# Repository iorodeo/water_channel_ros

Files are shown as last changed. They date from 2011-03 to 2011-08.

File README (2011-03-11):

# Install Ubuntu:
# http://www.ubuntu.com/desktop/get-ubuntu/download
# ubuntu-10.10-desktop-amd64

# Install Ubuntu packages
sudo apt-get install build-essential python-yaml cmake subversion wget python-setuptools mercurial

# ROS Installation
sudo sh -c 'echo "deb http://packages.ros.org/ros/ubuntu maverick main" > /etc/apt/sources.list.d/ros-latest.list'
wget http://packages.ros.org/ros.key -O - | sudo apt-key add -
sudo apt-get update
sudo apt-get install ros-diamondback-desktop-full

# Install the standalone program rosinstall
sudo easy_install -U rosinstall
sudo chmod -R a+rwx /usr/local/lib/python2.6/dist-packages/rosinstall*

# Clone water_channel_ros respository into ~/mercurial/
# Instructions at https://bitbucket.org/iorodeo/water_channel_ros/

# Install water_channel_ros from local repository
cd ~
mkdir ros
rosinstall ~/ros/ /opt/ros/diamondback
rosinstall ~/ros/ ~/mercurial/water_channel_ros/
echo "source ~/ros/setup.bash" >> ~/.bashrc

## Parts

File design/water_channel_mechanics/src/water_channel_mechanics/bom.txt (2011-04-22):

-*- mode:org -*-
#====================================================================#
#============================= bom.txt ==============================#
#                                                                    #
# Autogenerated using ros_cad. Hand editing this file is not         #
# advisable as all modifications will be lost when the program which #
# generated this file is re-run.                                     #
#====================================================================#

| ! | item number | name | description | dimensions | vendor | part number | quantity | cost |
|-
| | 1 | airbearing_mount_plate | Mounts air bearing carriage to t_slotted beam | x: 7.000, y: 7.500, z: 0.500 | ? | ? | 1 | 0.00 |
| | 2 | loadcell_mount_plate | Mounts loadcell to t_slotted beams | x: 6.000, y: 1.000, z: 0.125 | ? | ? | 2 | 0.00 |
| | 3 | pillowblock_mount_plate | Mounts pillowblocks to sleds | x: 7.750, y: 5.000, z: 0.250 | ? | ? | 10 | 0.00 |
| | 4 | slider_mount_plate | Mounts t_slotted beams to air bearing slider | x: 1.000, y: 6.000, z: 0.125 | ? | ? | 2 | 0.00 |
| | 5 | pillowblock | Rail bearings and mounts | x: 4.750, y: 3.500, z: 3.750 | LeeLinear | SPB-24-OPN | 10 | 0.00 |
| | 6 | 1010-double | T-Slotted L Bracket | bracket_type: double | McMaster | 47065T169 | 12 | 5.58 |
| | 7 | 1010-single | T-Slotted L Bracket | bracket_type: single | McMaster | 47065T223 | 32 | 3.98 |
| | 8 | 2020-double | T-Slotted L Bracket | bracket_type: double | McMaster | 47065T176 | 16 | 5.96 |
| | 9 | cushion | Protects the air bearing carriage | x: 1.500, y: 6.500, z: 0.250 | McMaster | 9013K153 | 2 | 15.94 |
| | 10 | submersible_mount | Holds the submersible tube | x: 3.000, y: 2.125, z: 2.000 | McMaster | 47065T207 | 1 | 51.91 |
| | 11 | laser_sensor_long_range | Micro-Epsilon optoNCDT ILR long range distance sensor | x: 5.670, y: 3.898, z: 2.008 | Micro-Epsilon | ILR1182-30(01) | 1 | 0.00 |
| | 12 | laser_sensor_short_range | Micro-Epsilon short range distance sensor | 100mm | Micro-Epsilon | optoNCDT1302 | 1 | 0.00 |
| | 13 | RAB6 | Non-motorized air bearing slide | slide travel: 4 | Nelson Air Corp. | RAB6 | 1 | 4095.00 |
| | 14 | laser_sensor_long_range_mount_plate_bottom | Mounts long range laser sensor to t_slotted beams | x: 4.000, y: 7.000, z: 0.236 | Pololu | ? | 1 | 0.00 |
| | 15 | laser_sensor_long_range_mount_plate_top | Mounts long range laser sensor to t_slotted beams | x: 4.000, y: 7.000, z: 0.236 | Pololu | ? | 1 | 0.00 |
| | 16 | laser_sensor_long_range_target_plate | Target for the long range distance sensor | x: 10.000, y: 10.000, z: 0.236 | Pololu | ? | 1 | 0.00 |
| | 17 | laser_sensor_short_range_mount_plate | Mounts short range laser sensor to t_slotted beams | x: 3.250, y: 4.250, z: 0.236 | Pololu | ? | 1 | 0.00 |
| | 18 | laser_sensor_short_range_target_plate | Target for the short range distance sensor | x: 6.000, y: 4.250, z: 0.236 | Pololu | ? | 1 | 0.00 |
| | 19 | 1010-003.000 | T-Slotted Extrusion | l: 3.000 | Prime Resource | ? | 4 | 0.00 |
| | 20 | 1010-005.000 | T-Slotted Extrusion | l: 5.000 | Prime Resource | ? | 2 | 0.00 |
| | 21 | 1010-006.000 | T-Slotted Extrusion | l: 6.000 | Prime Resource | ? | 5 | 0.00 |
| | 22 | 1010-010.624 | T-Slotted Extrusion | l: 10.624 | Prime Resource | ? | 4 | 0.00 |
| | 23 | 1020-006.000 | T-Slotted Extrusion | l: 6.000 | Prime Resource | ? | 1 | 0.00 |
| | 24 | 1020-008.000 | T-Slotted Extrusion | l: 8.000 | Prime Resource | ? | 3 | 0.00 |
| | 25 | 2040-032.000 | T-Slotted Extrusion | l: 32.000 | Prime Resource | ? | 1 | 0.00 |
| | 26 | 2040-050.000 | T-Slotted Extrusion | l: 50.000 | Prime Resource | ? | 3 | 0.00 |
| | 27 | test_submersible | Submersible used for testing | 12V | Sevylor | U120BLK-00-000 | 1 | 39.99 |
| | 28 | loadcell | Low Single PT Load Cell | 2Kg | TransducerTechniques | LSP-2 | 1 | 110.00 |
|-
| # | | | | | | | total |:=(@I$quantity..@II$quantity)*(@I$cost..@II$cost);%.2f;N

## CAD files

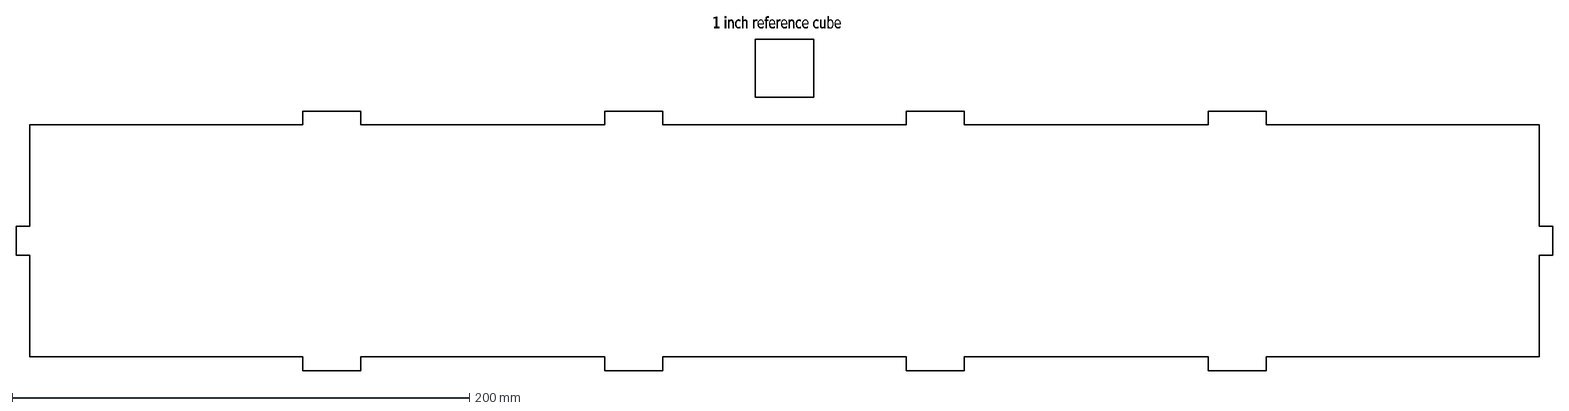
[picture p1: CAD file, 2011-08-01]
design/enclosures/dxf/controller_enclosure/v1p0/controller_enclosure_front.dxf
1\~inch\~reference\~cube

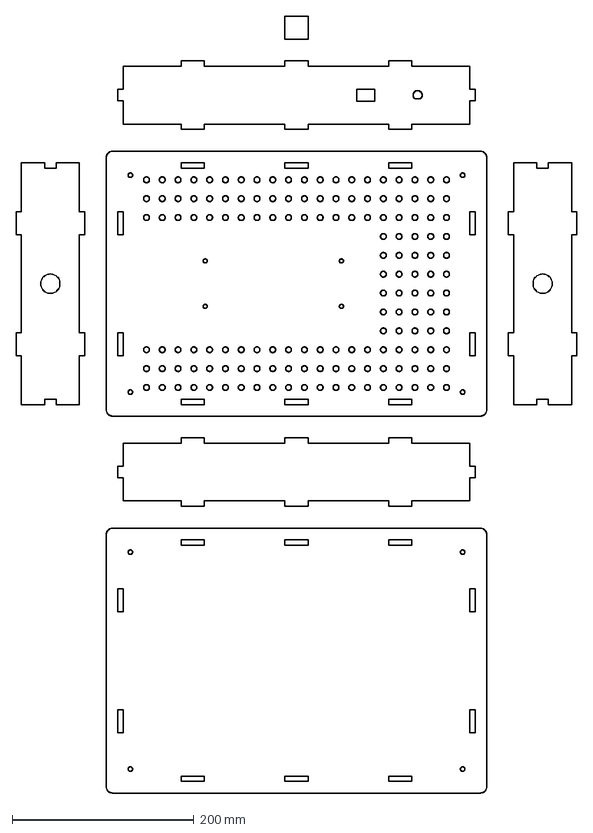
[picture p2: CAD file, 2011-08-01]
design/enclosures/dxf/test_motor_enclosure/v1p0/test_motor_enclosure.dxf
617.4 x 855.2 mm

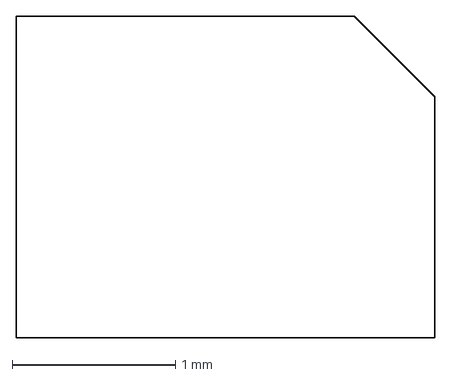
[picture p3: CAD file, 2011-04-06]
design/water_channel_mechanics/src/water_channel_mechanics/laser_sensor_short_range/laser_sensor_short_range.dxf
2.56 x 1.97 mm

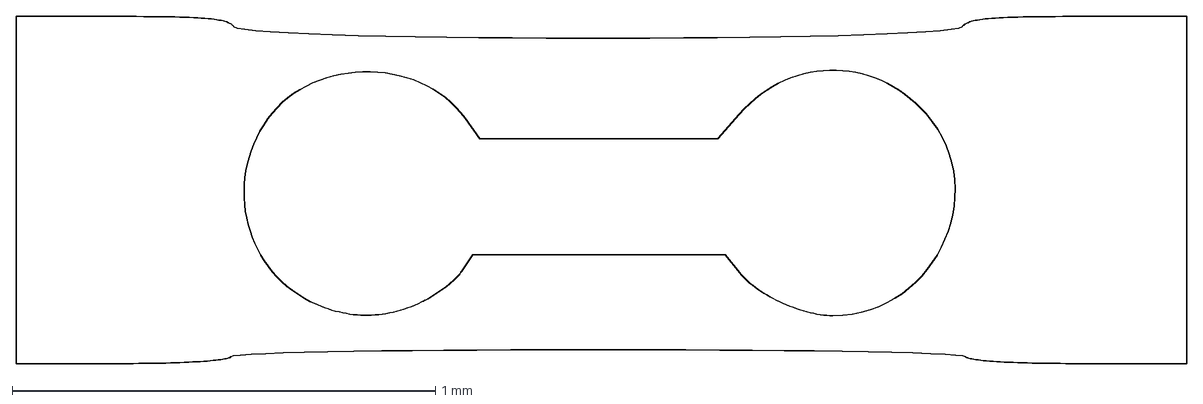
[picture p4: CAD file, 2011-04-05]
design/water_channel_mechanics/src/water_channel_mechanics/loadcell/loadcell.dxf
2.77 x 0.82 mm

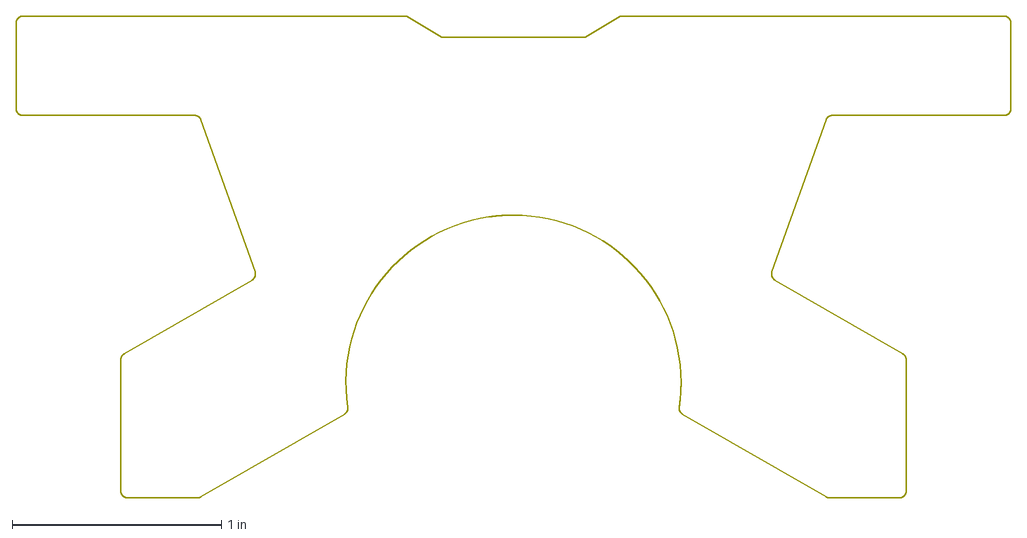
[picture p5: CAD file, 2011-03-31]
design/water_channel_mechanics/src/water_channel_mechanics/pillowblock/pillowblock.dxf
4.75 x 2.30 in

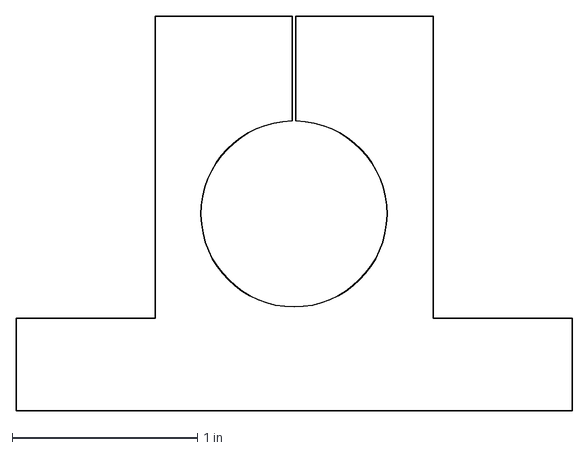
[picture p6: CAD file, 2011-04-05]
design/water_channel_mechanics/src/water_channel_mechanics/submersible_mount/submersible_mount.dxf
3.00 x 2.13 in

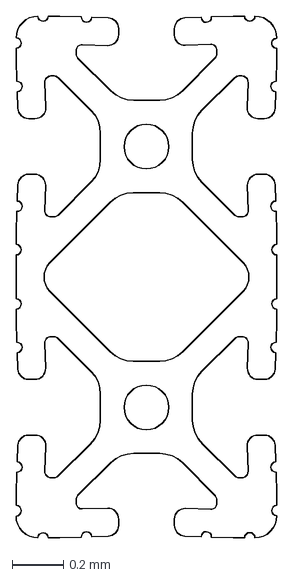
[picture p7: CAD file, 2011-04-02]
design/water_channel_mechanics/src/water_channel_mechanics/t_slotted/extrusion/1020.dxf
1.02 x 2.03 mm

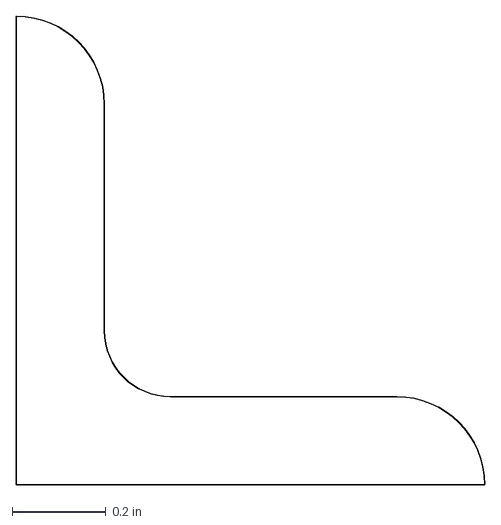
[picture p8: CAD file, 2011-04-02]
design/water_channel_mechanics/src/water_channel_mechanics/t_slotted/lbracket/1010.dxf
1.00 x 1 in

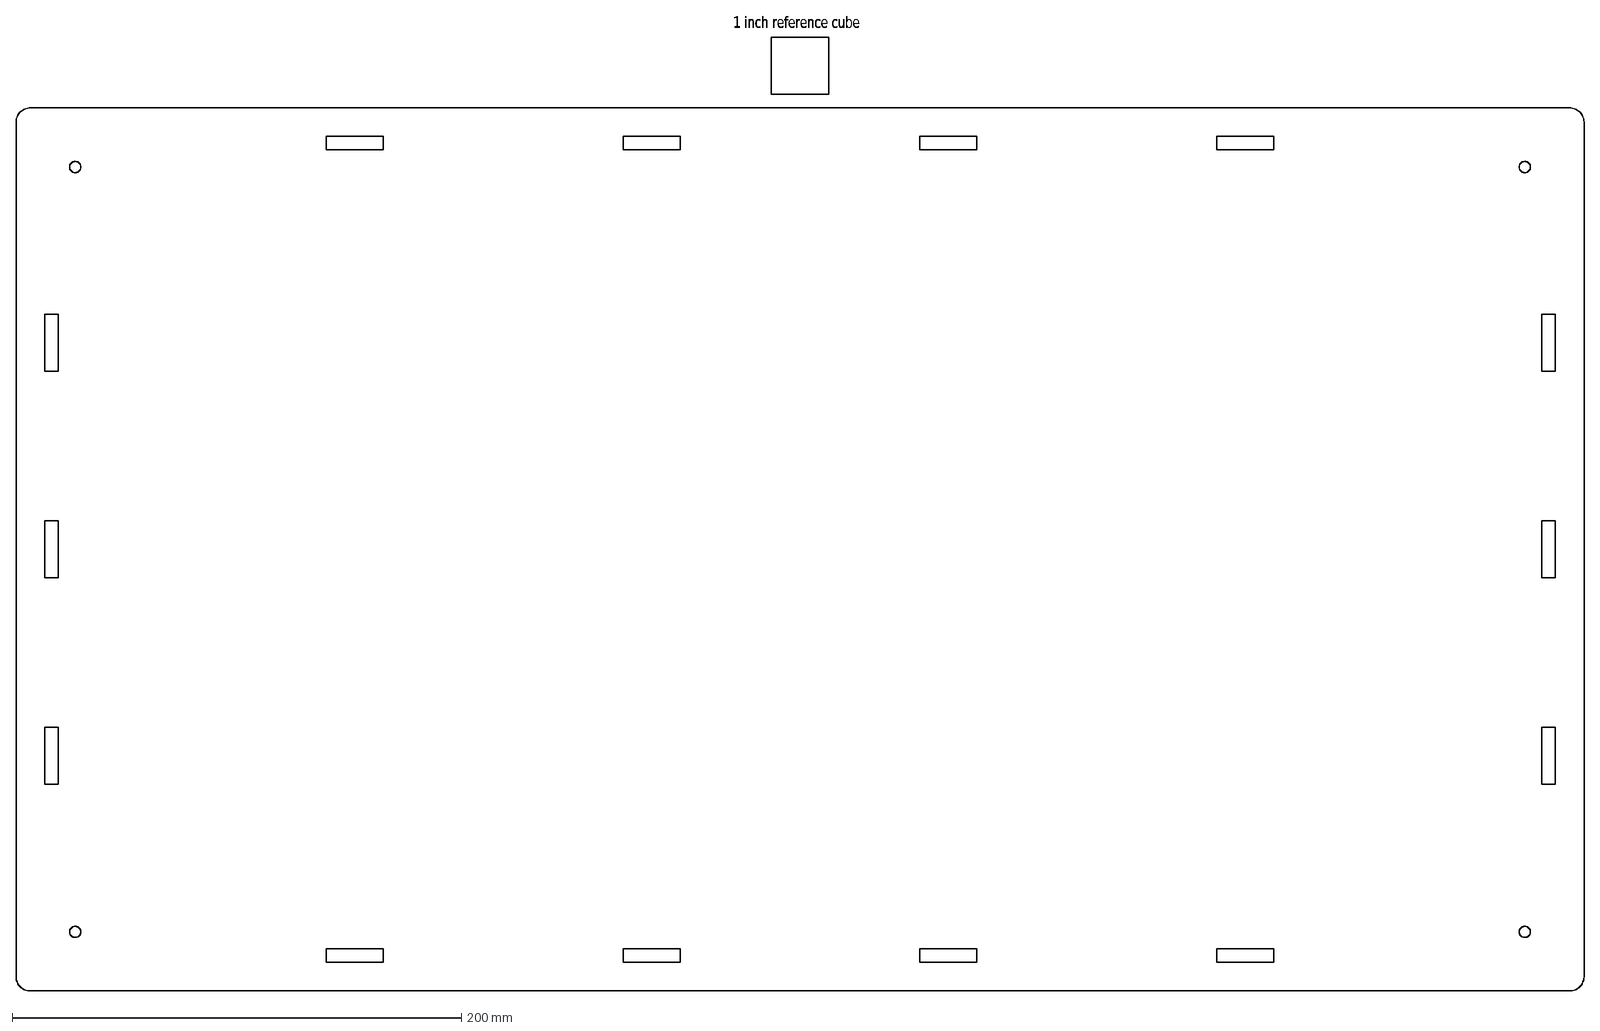
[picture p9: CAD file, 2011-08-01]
design/enclosures/dxf/controller_enclosure/v1p0/controller_enclosure_top.dxf
1\~inch\~reference\~cube

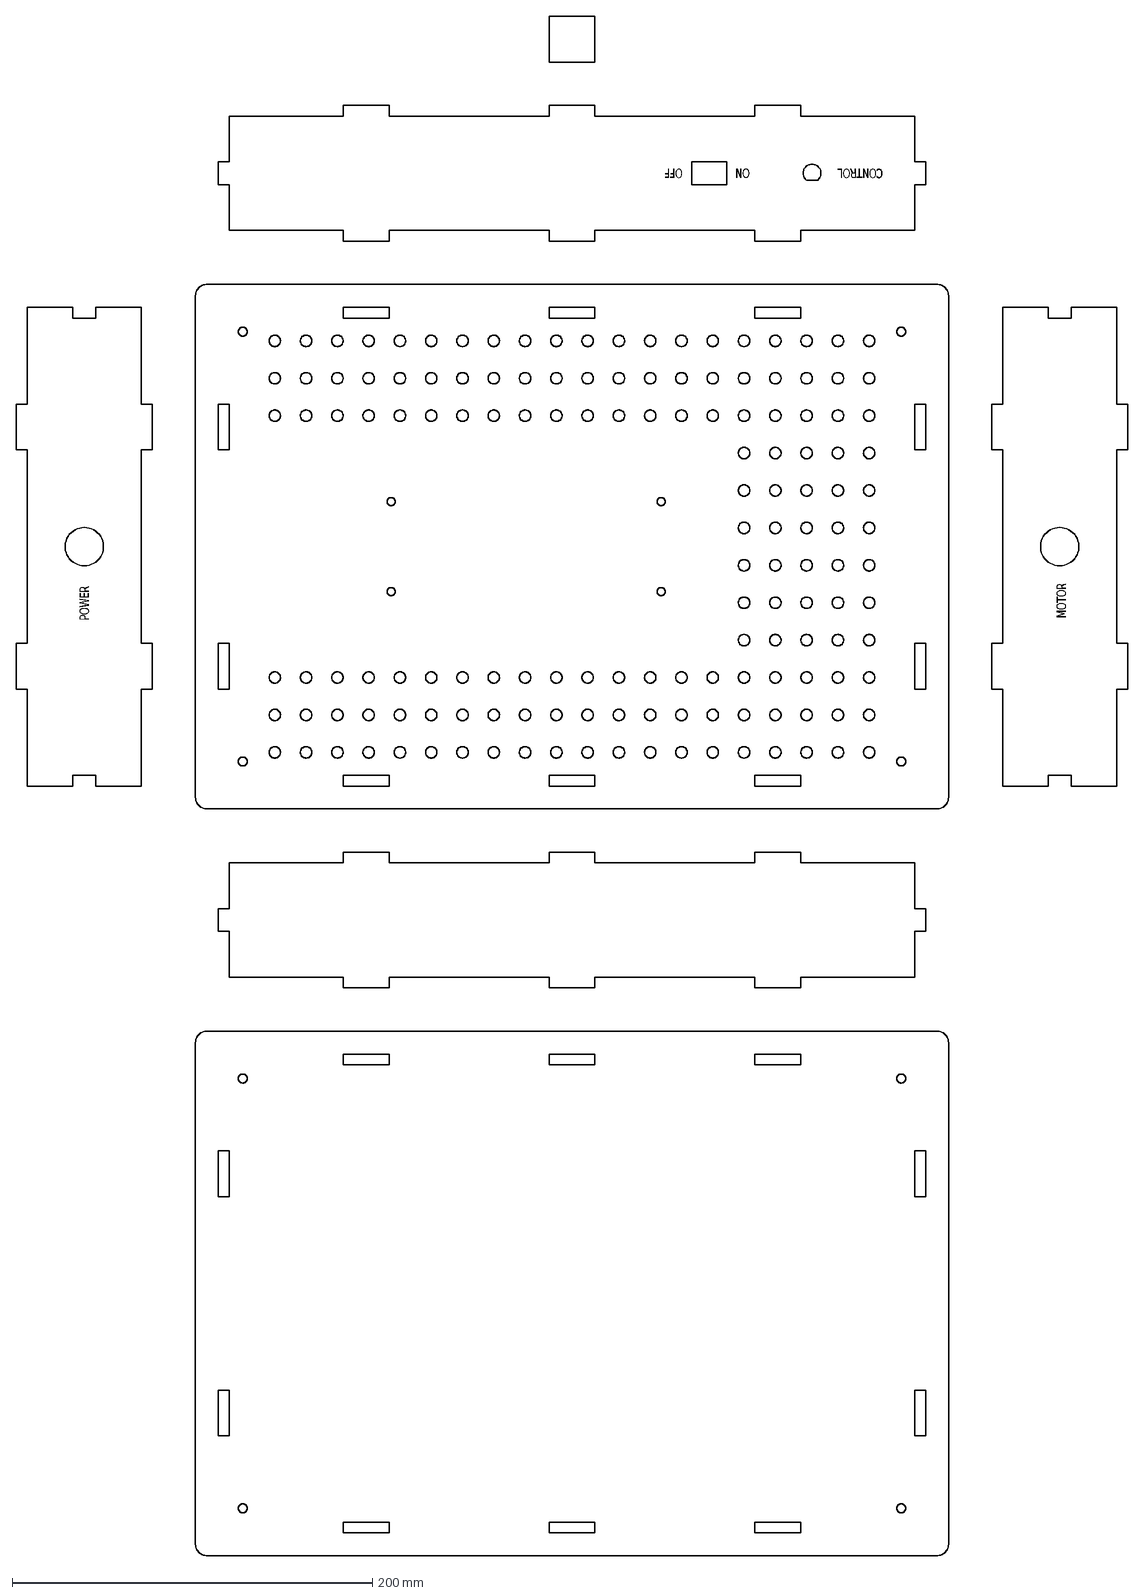
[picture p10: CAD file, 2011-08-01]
design/enclosures/dxf/test_motor_enclosure/v1p0/test_motor_enclosure_w_engrave.dxf
POWER
CONTROL
ON
OFF
MOTOR

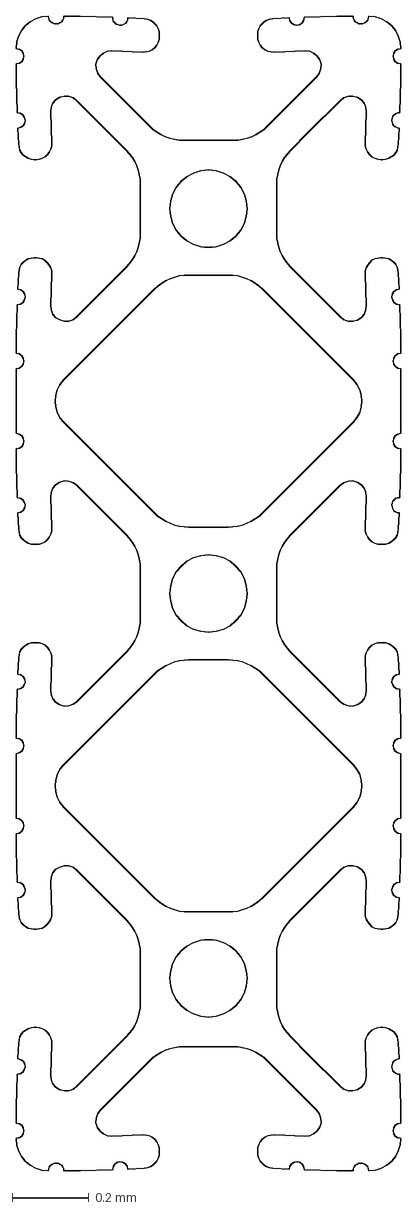
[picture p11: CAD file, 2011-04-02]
design/water_channel_mechanics/src/water_channel_mechanics/t_slotted/extrusion/1030.dxf
1.00 x 3.00 mm

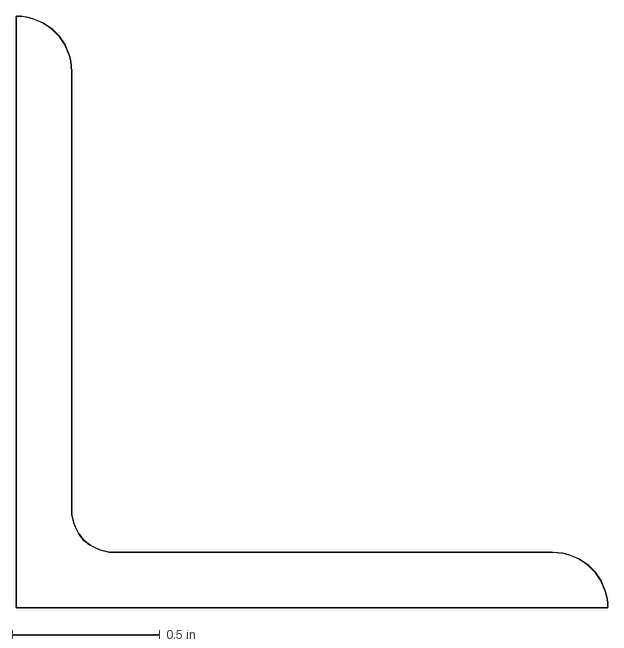
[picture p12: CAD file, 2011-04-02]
design/water_channel_mechanics/src/water_channel_mechanics/t_slotted/lbracket/2020.dxf
2.00 x 2.00 in

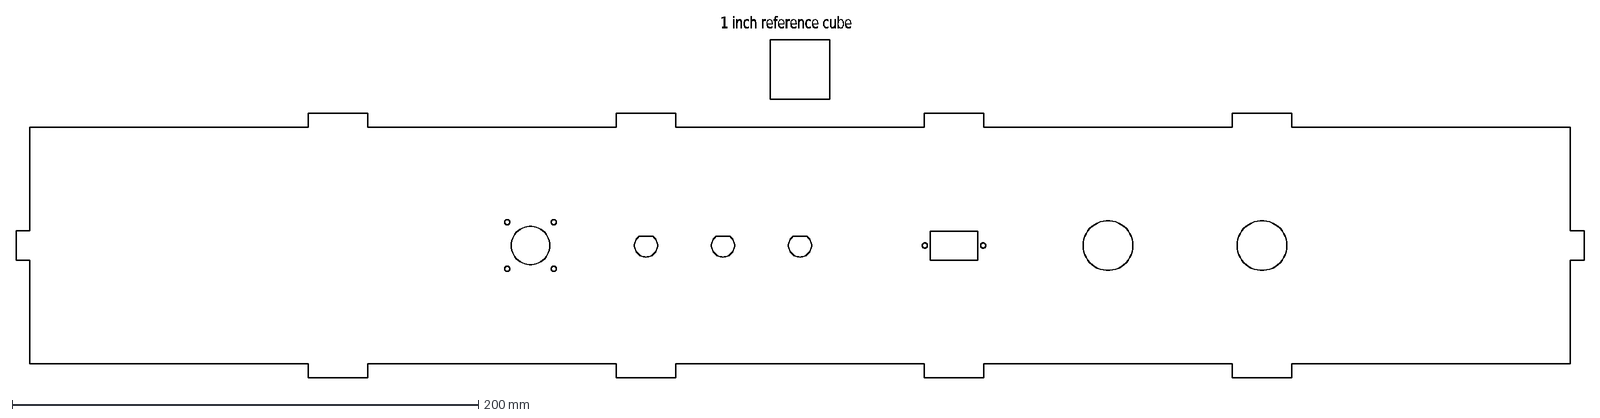
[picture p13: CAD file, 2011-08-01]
design/enclosures/dxf/controller_enclosure/v1p0/controller_enclosure_back.dxf
1\~inch\~reference\~cube

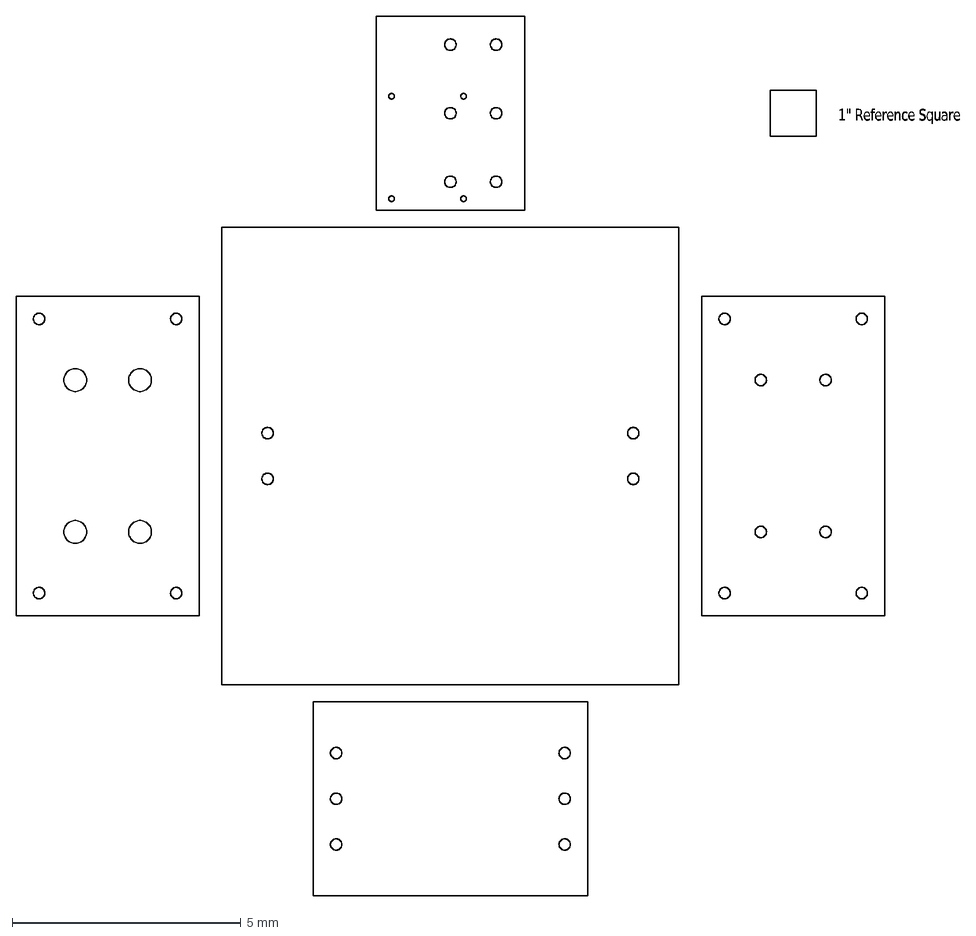
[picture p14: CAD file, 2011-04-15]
design/water_channel_mechanics/src/water_channel_mechanics/export_files/laser_cut_parts.dxf
1"\~Reference\~Square

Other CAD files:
design/enclosures/dxf/kill_switch_enclosure/kill_switch_enclosure.dxf
design/water_channel_mechanics/src/water_channel_mechanics/export_files/cushion.dxf
design/water_channel_mechanics/src/water_channel_mechanics/export_files/cushion_mm.dxf
design/water_channel_mechanics/src/water_channel_mechanics/t_slotted/extrusion/3060.dxf
design/enclosures/dxf/controller_enclosure/v1p0/controller_enclosure_bottom.dxf
design/enclosures/dxf/controller_enclosure/v1p0/controller_enclosure_left.dxf
design/enclosures/dxf/controller_enclosure/v1p0/controller_enclosure_right.dxf
design/water_channel_mechanics/src/water_channel_mechanics/export_files/airbearing_mount_plate.dxf
design/water_channel_mechanics/src/water_channel_mechanics/export_files/airbearing_mount_plate.stl
design/water_channel_mechanics/src/water_channel_mechanics/export_files/loadcell_mount_plate.dxf
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

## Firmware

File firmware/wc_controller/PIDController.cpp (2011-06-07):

#include "PIDController.h"

PIDController::PIDController() {
    pGain = 0.0;
    dGain = 0.0;
    iGain = 0.0;
    ffGain = 0.0;
    lastError = 0.0;
    integralTerm = 0.0;
    isFirstUpdate = true;
    outputMax = PID_DFLT_OUTPUT_MAX;
    outputMin = PID_DFLT_OUTPUT_MIN;
}

float PIDController::update(float error, float ffValue) {
    float output;
    float proportionalTerm;
    float derivativeTerm;
    float feedForwardTerm;
    if (isFirstUpdate == true) {
        lastError = error;
        isFirstUpdate = false;
    }
    proportionalTerm = pGain*error;
    integralTerm += iGain*error;
    integralTerm = clamp(integralTerm);
    derivativeTerm = dGain*(error - lastError);
    //feedForwardTerm = ffGain*ffValue;
    feedForwardTerm = feedForwardFunc(ffValue);
    output = proportionalTerm + integralTerm + derivativeTerm + feedForwardTerm;
    output = clamp(output);
    lastError = error;
    return output;
}

void PIDController::reset() {
    lastError = 0.0;
    integralTerm = 0.0;
    isFirstUpdate = true;
}

void PIDController::setGains(float _pGain, float _iGain, float _dGain, float _ffGain) {
    pGain = _pGain;
    iGain = _iGain;
    dGain = _dGain;
    ffGain = _ffGain;
}

void PIDController::setPGain(float _pGain) {
    pGain = _pGain;
}

void PIDController::setIGain(float _iGain) {
    iGain = _iGain;
}

void PIDController::setDGain(float _dGain) {
    dGain = _dGain;
}

void PIDController::setFFGain(float _ffGain) {
    ffGain = _ffGain;
}

void PIDController::setOutputLimits(float minValue, float maxValue) {
    if (minValue > maxValue) return;
    outputMin = minValue;
    outputMax = maxValue;
}

float PIDController::clamp(float value) {
    float clampedValue;
    if (value > outputMax) {
        clampedValue = outputMax;
    }
    else if (value < outputMin) {
        clampedValue = outputMin;
    }
    else {
        clampedValue = value;
    }
    return clampedValue;
}

float PIDController::feedForwardFunc(float ffValue) {
    const float pos_ff_coeff = 5.375;
    const float pos_ff_offset = 93.0;
    const float neg_ff_coeff = 5.40;
    const float neg_ff_offset = -69.35;
    float retValue;
    if (ffValue > 0) {
        retValue = pos_ff_coeff*ffValue + pos_ff_offset;
    }
    else if (ffValue < 0) {
        retValue = neg_ff_coeff*ffValue + neg_ff_offset; 
    }
    else {
        retValue = 0.0;
    }
    return retValue;
}

        

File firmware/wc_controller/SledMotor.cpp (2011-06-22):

#include "WProgram.h"
#include "SledMotor.h"

void SledMotor::initializeIO() {
    // Create Analog output
    analogOut = MCP4822(AOUT_CS,AOUT_LDAC);

    // Configure analog outputs
    analogOut.setGain2X_AB();

    // Set SSR pins to output mode
    pinMode(SSR0,OUTPUT);
    pinMode(SSR1,OUTPUT);

    off();
}

void SledMotor::setVelocity(int value) {
    int modValue;
    modValue = deadBandComp(value);
    modValue = clamp(modValue);
    setDirection(modValue);
    setSpeed(modValue);
}

void SledMotor::setVelocity(float value) {
    float clampedValue;
    int intValue;
    clampedValue = clamp(value);
    intValue = (int) clampedValue;
    setVelocity(intValue);
}

void SledMotor::off() {
    // Set analog output value to zero and both direction lines to low.
    analogOut.setValue_A(0);
    digitalWrite(SSR0,LOW);
    digitalWrite(SSR1,LOW);
}

void SledMotor::setSpeed(int value) {
    int absValue;
    absValue = abs(value);
    analogOut.setValue_A(absValue);
}


void SledMotor::setDirection(int value) {
    if (value > 0) {
        digitalWrite(SSR1,LOW);
        digitalWrite(SSR0,HIGH);
    }
    else if (value < 0) {
        digitalWrite(SSR0,LOW);
        digitalWrite(SSR1,HIGH);
    }
    else {
        digitalWrite(SSR0,LOW);
        digitalWrite(SSR1,LOW);
    }
}

int SledMotor::clamp(int value) {
    int clampedValue;
    if (value > SM_MOTOR_CMD_CLAMP) {
        clampedValue = SM_MOTOR_CMD_CLAMP;
    }
    else if (value < -SM_MOTOR_CMD_CLAMP) {
        clampedValue = -SM_MOTOR_CMD_CLAMP;
    }
    else {
        clampedValue = value;
    }
    return clampedValue;
}

float SledMotor::clamp(float value) {
    static float sm_motor_cmd_clamp = (float) SM_MOTOR_CMD_CLAMP;
    float clampedValue;

    if (value > sm_motor_cmd_clamp) {
        clampedValue = sm_motor_cmd_clamp;
    }
    else if (value < -sm_motor_cmd_clamp) {
        clampedValue = -sm_motor_cmd_clamp;
    }
    else {
        clampedValue = value;
    }
    return clampedValue;
}

int SledMotor::deadBandComp(int value) {
    int compValue;
    compValue = value;
    if (compValue > 0) {
        compValue += SM_DRIVE_DEADBAND;
    }
    if (compValue < 0) {
        compValue -= SM_DRIVE_DEADBAND;
    }
    return compValue;
}

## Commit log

2011-03-31 Added initial roscad parts to the water channel assembly
    [pillowblock.dxf]
2011-04-02 Finished pillowblock_mount_plate and motorized_sled
2011-04-02 Added t_slotted dxf profiles and updated parts
    [1010.dxf, 1020.dxf, 1030.dxf, 1545.dxf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]
2011-04-05 Added many parts...
    [loadcell.dxf, submersible_mount.dxf]
2011-04-06 Added parts...
    [laser_sensor_short_range.dxf]
2011-04-06 Finished most of the mechanical design
    [laser_sensor_short_range.dxf]
2011-04-14 Modified bom parameters and added long range distance sensor
2011-04-15 Finished the design of most of the parts. Included exported parts
    [airbearing_mount_plate.stl, loadcell_mount_plate.stl, pillowblock_mount_plate.stl, slider_mount_plate.stl]
2011-04-15 Added export files and moved them to export_files/
    [airbearing_mount_plate.stl, laser_cut_parts.dxf, loadcell_mount_plate.stl, pillowblock_mount_plate.stl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]
2011-04-22 Added dxf output files
    [airbearing_mount_plate.dxf, loadcell_mount_plate.dxf, pillowblock_mount_plate.dxf, slider_mount_plate.dxf]
2011-05-27 Added cushion.dxf files
    [cushion.dxf, cushion_mm.dxf]
2011-05-31 Added controller and distance_118x packages. Removed laser_rangefinder.
2011-06-01 Added arduino firmware.
2011-06-02 Added fakeit options to laser distance sensor - for developing when no sensor is available.
2011-06-04 Added "motor command" mode to controller for system testing.
2011-06-06 Added motor_cmd_source ros package for openloop testing.
2011-06-07 Added data_loggers package. Created a simple motor_cmd data logger an launch file for open loop testing.
2011-06-16 Added Kalman filter to distance sensor node to get better velocity estimates.
2011-06-17 Modified so that kalman filter estimates of position and velocity are sent to the controller. This is the first step in switch the captive trajectory system to a velocity controller - might include s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
2011-06-24 Added gain scheduling controller. Added motor command sin source for testing.
2011-06-30 Added enclosure designs for controller and test motor electronics.
2011-07-01 Finished test motor enclosure. Worked on controller enclosure.
    [test_motor_enclosure.dxf, test_motor_enclosure_w_engrave.dxf]
2011-07-09 Finished design of controller enclosure.
2011-07-14 Finalize controller enclosure design. Add version 1.0 of the dxf files for the enclosure designs.
    [controller_enclosure_back.dxf, controller_enclosure_bottom.dxf, controller_enclosure_front.dxf, controller_enclosure_left.dxf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]
2011-08-02 Added streaming of force sensor and short range laser sensor data to host PC. Still need to set up topic for these values which the sled IO node will broadcast on.
2011-08-04 Some major directory rearrangment. Added analog input message type.
    [1010.dxf, 1020.dxf, 1030.dxf, 1545.dxf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]
2011-08-08 Finished first version of captive trajectory system which uses force sensor. First complete test. Started working of filters package - to unify filter development. We will probably want a lowpass ver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
2011-08-08 Removed filtersls package - typo in name.
2011-08-08 Added filters package.
2011-11-27 Added services for setting the maximum percent velocity for the motor_cmd_joystick node. Added ability to set the sled bounds form the GUI. Changed ModeSwitcher class to RobotControl class - as this 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
2012-01-23 Created enclosure for kill switch.
    [kill_switch_enclosure.dxf]
2012-05-08 Added matplotlib backend specification, Qt4Agg, to GUI. Moved old launch files temporarliy to filters package as they were conflicting with existing launch file.
2012-05-10 Worked on laser setpt node for inertial trajectory mode.
2012-05-10 Added launch file for laser set point source node.
2012-05-10 Added distance sensor watchdog.
2012-05-11 Added Kalman filter to laser setpt source. Added ability to set gain on contoller.
2012-12-20 Added lowpass filter to force_source.
